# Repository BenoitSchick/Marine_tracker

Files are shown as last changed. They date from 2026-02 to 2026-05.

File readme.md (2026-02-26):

# 🌊 PI MONIT – Group 4  
## Marine Animal Tracking System  

**Schick Benoit · Warpelin Daryl · Jeyapalan Jeyapiragash · Zweifel Robin**

---

## 📌 Project Overview

This project focuses on the design of an embedded tracking module intended to be attached to marine animals.

The primary objective is to monitor animal movements in order to:

- Better understand behavioural patterns  
- Analyse migratory routes  
- Identify critical marine areas requiring protection  

Beyond behavioural research, marine animals provide a unique and valuable platform for carrying environmental sensors. Their ability to travel long distances and dive to great depths enables data collection in regions that are difficult — or impossible — for humans to access.

Our system is designed to measure **ocean temperature as a function of depth**, contributing to climate research. Ocean temperature plays a crucial role in regulating ocean currents, which in turn significantly influence the planet’s global thermal balance.

The device must satisfy both **animal tracking** and **oceanographic measurement** requirements, while operating reliably under extreme marine conditions.

---

## 🌊 Mechanical & Environmental Constraints

The module must withstand harsh deep-sea conditions for extended periods.

### Pressure Resistance

- Fully waterproof housing  
- Designed to resist pressures equivalent to **1,000 m depth** (to be confirmed)  
- Some marine species dive beyond 1,000 m  

### Corrosion & Environmental Resistance

- Long-term exposure to seawater  
- Resistance to:
  - Salinity  
  - Thermal variations  
  - Biological fouling  

### Duration

- Minimum operational lifespan: **1 month**  
- Corresponds to a typical migration cycle  

### Structural Integrity

- Housing must maintain mechanical integrity despite:
  - High pressure  
  - Temperature changes  
  - Continuous environmental stress  

---

## ⚡ Electronic Constraints & Specifications

The embedded system must operate autonomously for at least **one month**.

### Power Optimization Strategy

- Optimised electronic architecture  
- Deep sleep operating modes  
- Careful selection of ultra-low-power components  

### Required Sensors

The module must integrate:

- 🌡️ **Temperature sensor**  
- 📏 **Pressure sensor** (for depth measurement and data validation)

These measurements form the foundation of the ocean monitoring component of the project.

---

## 📍 Localisation System

A GPS module must be integrated to:

- Track the animal’s position  
- Associate environmental measurements with precise geographic coordinates  

Position data is essential for accurate mapping and scientific analysis.

---

## 📡 Data Communication

When the animal surfaces, the module must transmit collected data.

Because the system operates in open ocean environments, communication must be achieved via:

- 🛰️ **Satellite link** (global coverage solution)

The transmitted data is then:

- Stored in a central database  
- Prepared for processing and analysis  

---

## 📊 Data Processing & Visualisation

Collected data will be:

1. Processed and validated  
2. Made accessible via a web platform  
3. Presented through interactive visualisations  

The platform must also:

- Provide access to raw scientific data  
- Enable collaboration within the research community  

The final repository could be based on the EMODnet portal  
(European Marine Observation and Data Network).

---

## 🎯 Project Goals Summary

- ✔ Long-term autonomous marine monitoring  
- ✔ Behavioural tracking of marine species  
- ✔ Ocean temperature profiling by depth  
- ✔ Satellite-based data transmission  
- ✔ Open scientific data access  
- ✔ Contribution to climate research  

---

> PI MONIT aims to combine embedded systems engineering, oceanography, and data science to support marine conservation and climate research.

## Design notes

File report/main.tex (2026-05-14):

\documentclass[12pt]{article}

% Language setting
% Replace `english' with e.g. `spanish' to change the document language
\usepackage[T1]{fontenc}
\usepackage[english]{babel}

% Set page size and margins
% Replace `letterpaper' with`a4paper' for UK/EU standard size
\usepackage[a4paper,top=2.5cm,bottom=2.5cm,left=2cm,right=2cm,marginparwidth=1.75cm]{geometry}

% include graphics i.e images
\usepackage{graphicx}
\usepackage{fancyhdr} % headers
\usepackage[utf8]{inputenc}
\usepackage{gensymb}
\usepackage{subcaption}
\usepackage{array}
\usepackage{tabularx}
\usepackage{csvsimple}
\usepackage{titlesec}
\usepackage{lastpage}
\usepackage{pdfpages}
\usepackage{comment}
\usepackage{xcolor}
\usepackage{multirow}
\usepackage{verbatim}
\usepackage{bm}
% \usepackage{gensymb}
\usepackage{url}
\usepackage{amsmath}

\usepackage{lipsum}  

\setcounter{tocdepth}{1} % Exclude subsubsections from the table of contents

% include hyperlinks in the doc
\usepackage{hyperref}
%setup hyperref

\pagestyle{fancy}
\fancyhf{}
\rhead{\today}
\lhead{Marine Animal Tracking System}
\lfoot{PI - Wearable Sensing Device}
\rfoot{Page \thepage}
\renewcommand{\headrulewidth}{1pt}
\renewcommand{\footrulewidth}{1pt}

%------------------------------------------------------------------------------------------------
\title{PI}
\author{Benoit Schick}

\begin{document}

\begin{titlepage}
   \begin{center}
        \Huge
        Marine Animal Tracking System\\
        \Large 
        PI - Wearable Sensing Device 
            
        \vspace{1.5cm}
        \Large    
        Benoit Schick\\
        Warpelin Daryl\\
       	Jeyapalan Jeyapiragash\\
	Zweifel Robin
        
        \vspace{0.5cm}
        
        Supervisor:\\
        \vspace{0.1cm}
        Marco Mazza\\

        \vfill

        2024–2025 Academic Year, Spring Semester \\
        \vspace{1cm}
            
        \normalsize
        Multidisciplinary project\\
        \vspace{0.25cm}
        
	Master of science in Engineering 
        \vspace{0.25cm}
        
        \vspace{0.8cm}
            
        
        \vspace{1cm} 
        
   \end{center}
\end{titlepage}

\pagestyle{fancy}

\section{Hardware (Benoit Schick)}
\subsection{Défis et contraintes du système embarqué}

Le système développé dans ce projet doit fonctionner dans un environnement particulièrement contraignant, ce qui impose certains choix au niveau de l'architecture. 
\subsubsection{Isolement géographique}
L’une des contraintes fondamentales est la localisation des animaux suivis. Les espèces ciblées évoluent en haute mer, à des centaines voire des milliers de kilomètres de toute infrastructure terrestre. Dans ces zones, aucune technologie de communication classique n’est disponible : les réseaux cellulaires tels que le GSM, la 4G ou la 5G ne sont exploitables qu’à proximité des côtes, et les réseaux IoT longue portée comme LoRaWAN sont insuffisants pour cette application. \\
Dans ce contexte, la seule solution viable pour assurer une communication globale est la transmission par satellite. Deux technologies principales sont généralement utilisées dans ce type d’application :
\begin{itemize}
	\item \textbf{Le réseau Iridium} : Système qui repose sur une constellation de 66 satellites en orbite basse (LEO, ~780 km), offre une latence faible et une couverture totale.
	\item \textbf{Le réseau Argos} : Système satellite pour la localisation et la collecte de données désigné spécifiquement pour l'étude et la protection de l'environnement. Il est par exemple utilisé pour le suivi d'animaux marins et est largement adopté dans la communauté scientifique pour ce type d'application.  
\end{itemize}
Ces solutions permettent une communication globale mais introduisent des contraintes importantes en termes d’énergie et de disponibilité du signal.

\subsubsection{Contraintes du milieu marin}
Le milieu marin impose une contrainte majeure : l'eau de mer est un milieu extrêmement atténuant pour les ondes électromagnétiques utilisées pour la communication satellite. A quelques centimètres de profondeur seulement, tout signal est totalement absorbé et il est donc impossible de transmettre ou de recevoir quoi que ce soit lorsque l'animal est immergé, quelle que soit la puissance d'émission utillisée.\\
Cette contrainte impose un fonctionnement discontinu du système, alternant entre des phases d’immersion, où seules les mesures sont réalisées, et des phases de surface, où la communication est possible.

\subsubsection{Stockage temporaire}
L'impossibilité de transmission en continu des données exige d'intégrer une mémoire non volatile externe pour stocker temporairement l'ensemble des données acquises pendant les phases d'immersion (température, pression \footnote{Bien que fondamentale, la mesure de la pression a été abandonnée du à des contraintes budgétaires. Elle sera quand même évoquée dans ce rapport}, la position et horodatage des mesures). \\
Cette mémoire permet donc de gérer l’imprévisibilité des phases de surface, qui dépendent du comportement de l’animal et des conditions environnementales.

\subsubsection{Consommation}
Les conditions dans lequel le système va évoluer, introduit des contraintes importantes en termes de consommation énergétique. Les modules de communication, en particulier le GPS et le système satellite, figurent parmi les éléments les plus énergivores du système. \\
En effet, le module GPS nécessite une phase d’acquisition du signal satellite, qui peut devenir longue et coûteuse en énergie si les conditions de réception sont mauvaises ou si les fenêtres de surface sont très courtes. De même, le module de communication satellite présente des pics de consommation élevés lors de chaque tentative de transmission. \\
Ces contraintes sont aggravées par l’incertitude sur la durée et la fréquence des phases de surface, ce qui peut entraîner des activations répétées des modules de localisation et de communication, augmentant encore la consommation globale du système. \\

Or l’autonomie du système constitue un paramètre critique, car elle détermine la durée d’exploitation du dispositif ainsi que la capacité à le récupérer grâce au module GPS, chargé de transmettre la position du boîtier. Une stratégie de gestion énergétique est donc nécessaire afin de limiter le temps d'activation des modules GPS+satellite et maximiser le temps passé en mode low-power. Le système devra donc reposer sur une logique événementielle, dans laquelle les modules GPS et satellite ne sont activés que lorsque les conditions sont favorables, c’est-à-dire lors des phases de surface.

\subsection{Spécifications}

Le comportement de l’animal joue un rôle déterminant dans le dimensionnement du système. En effet, lorsqu’il est immergé, toute communication satellite est impossible. Le dispositif doit donc exploiter les phases de surface, durant lesquelles l’animal doit rester suffisamment longtemps pour permettre l’acquisition d’une position GPS ainsi que la transmission des données via le module satellite. La profondeur de plongée constitue également un paramètre critique, car elle impose des contraintes mécaniques importantes, notamment en raison de la pression exercée sur le boîtier. \\
Après comparaison avec d’autres espèces (cf. tableau), le choix s’est porté sur la tortue marine. Ce choix repose principalement sur ses phases de surface relativement régulières, qui facilitent l’établissement d’une connexion satellite fiable et limitent les activations inutiles des modules de communication et de localisation. Cela permet ainsi de réduire la consommation énergétique du système tout en simplifiant certaines contraintes mécaniques.\\

L’autonomie représente un autre enjeu majeur. Le système doit être capable de fonctionner sur une longue durée afin de collecter un volume de données suffisant, tout en permettant idéalement la récupération du dispositif en fin de mission afin de limiter son impact environnemental. Cela implique une gestion optimisée de l’énergie, notamment en réduisant l’utilisation des modules les plus énergivores.\\

% Enfin, l’environnement d’utilisation impose des contraintes fortes en termes de communication. En raison de l’éloignement des infrastructures terrestres, les solutions classiques (GSM, LoRa, etc.) ne sont pas exploitables. L’utilisation d’une liaison satellite est donc indispensable pour assurer la transmission des données sur de longues distances.

\noindent Voici un résumé des spécifications prises en compte pour la partie Hardware du projet :

\begin{itemize}
    \item \textbf{Communication} : Transmission des données via un réseau satellite.
    \item \textbf{Localisation} : Acquisition de la position GPS du dispositif afin de permettre sa localisation et sa récupération
    \item \textbf{Stockage} : Utilisation d'une mémoire non volatile permettant l’enregistrement des données durant les phases d’immersion.
    \item \textbf{Autonomie} : Fonctionnement sur batterie avec un objectif d’autonomie d’environ un mois, reposant sur une optimisation de la consommation (modes low power, activation événementielle des modules).
    \item \textbf{Capteurs} : Mesure de la température de l'eau et de la profondeur (via un capteur de pression) en fonction de la position, afin de constituer une base de données exploitable pour permettre de suivre l'évolution thermiques des océans dans le cadre du réchauffement climatique.  
\end{itemize}

\subsection{Architecture générale} 
La partie électronique doit assurer de manière autonome la localisation de l’animal, l’acquisition de données environnementales, le stockage temporaire des mesures ainsi que leur transmission vers une infrastructure terrestre via un lien satellite. L’ensemble de ces fonctions doit être garanti dans des conditions environnementales extrêmes (pression, salinité, immersion), tout en maintenant une autonomie énergétique suffisante.

\begin{figure}[h!]
	\centering
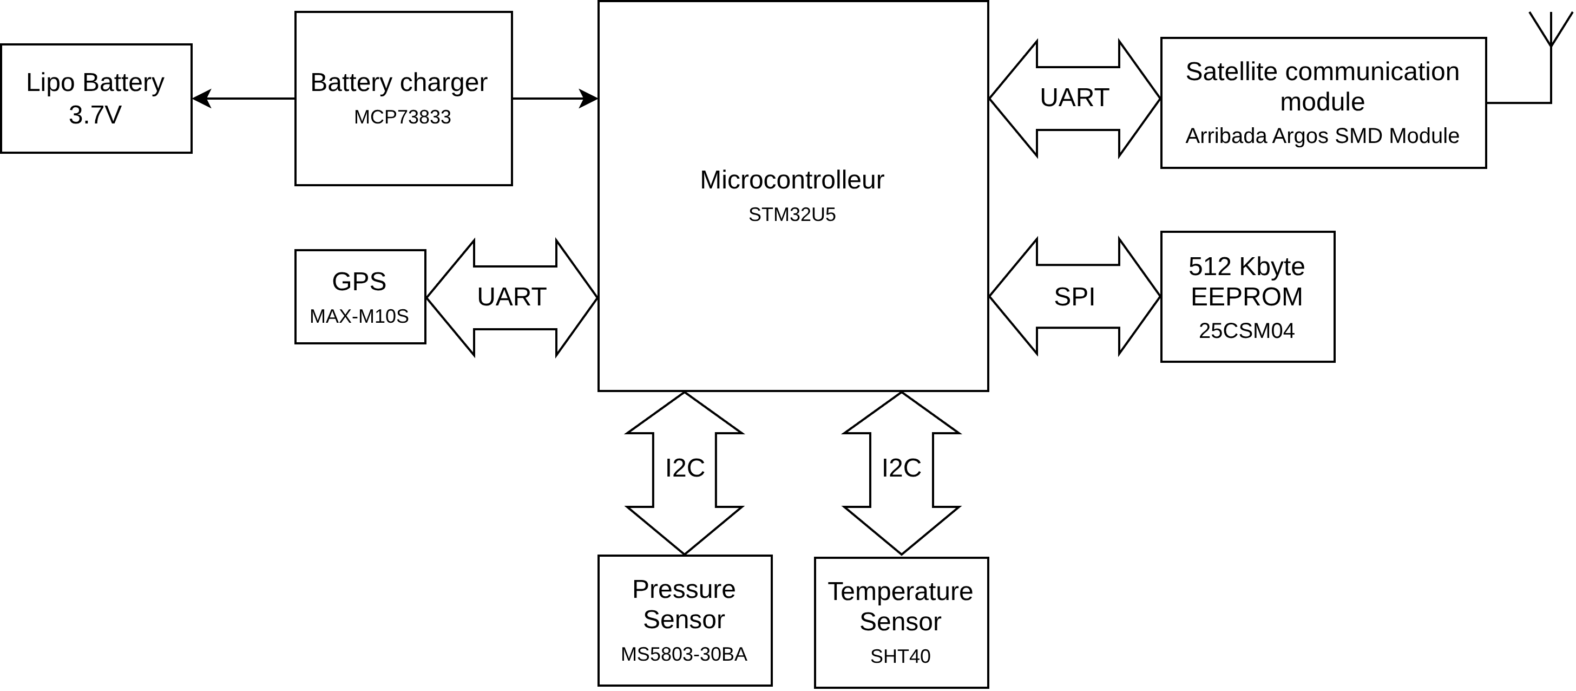
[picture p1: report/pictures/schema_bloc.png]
		
	\caption{Schéma bloc de la partie Hardware}
	\label{fig:schema_bloc}
\end{figure}

L’architecture du système s’articule autour d’un microcontrôleur STM32U5 basé sur un coeur ARM Cortex-M33. Ce composant a été retenu pour sa très faible consommation (jusqu’à 160 nA en mode low power), sa compatibilité avec Zephyr RTOS facilitant le développement logiciel, ainsi que la présence de multiples modes low-power (7 modes) permettant d’adapter le compromis entre consommation, disponibilité des périphériques et sources de wakeup. Il intègre également un large éventail d’interfaces de communication (I2C, SPI, UART, USB), assurant l’interconnexion avec les différents modules du système. \\

L’alimentation repose sur une batterie Lithium-Polymère (LiPo) 1S d’une capacité de 10 Ah. Ce choix s’explique par sa forte densité énergétique, permettant de optimiser l’énergie stockée tout en réduisant la masse et le volume (Fig. \ref{fig:densite_bat}), ce qui constitue un critère essentiel pour une application embarquée sur animal. Néanmoins, ce type de batterie impose des contraintes strictes en termes de sécurité et d'utilisation. \\
La gestion de la charge est assurée par le circuit MCP73833, qui intègre les protections nécessaires contre la surcharge et la décharge excessive. Dans cette phase de prototypage, la recharge s’effectue via une interface USB-C. À terme, une solution de récupération d’énergie est envisagée, basée sur un générateur entraîné par une hélice mise en rotation par les déplacements de l’animal.

\begin{figure}[h!]
	\centering
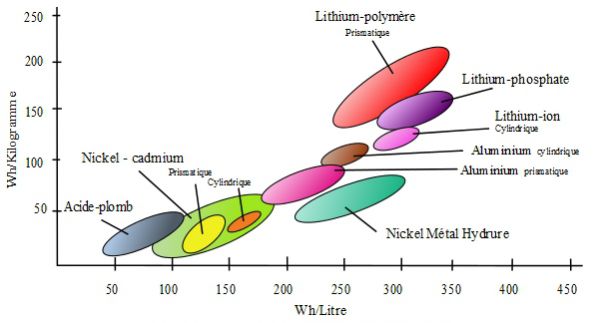
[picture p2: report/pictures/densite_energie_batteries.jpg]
		
	\caption{Densité d'énergie selon le type de batterie}
	\label{fig:densite_bat}
\end{figure}

La localisation est assurée par le module GPS MAX-M10S, sélectionné pour son faible niveau de consommation (environ 25mW en mode tracking continu), particulièrement adapté aux systèmes sur batterie. La communication avec le microcontrôleur s’effectue via une interface UART.\\
L’acquisition des données environnementales repose sur deux capteurs connectés au microcontrôleur via le bus I2C :
\begin{itemize}
	\item Capteur de pression MS5803-30BA : permet d’estimer la profondeur à partir de la pression mesurée. Sa capacité à supporter jusqu’à 30bar (environ 300m de profondeur) le rend adapté au suivi de tortues marines.
	\item Capteur de température et humidité SHT40 : mesure la température interne du boîtier ainsi que l’humidité, paramètre critique pour détecter toute infiltration. Ce capteur présente également une très faible consommation ($0.4\mu W$), compatible avec les contraintes énergétiques du système.
\end{itemize}

La transmission des données est assurée par un module de communication satellite Arribada Argos SMD, interfacé en UART avec le microcontrôleur. Ce module a été retenu pour son caractère open-source, facilitant l’intégration logicielle, ainsi que pour son coût plus accessible que les solutions Iridium. Il permet d’exploiter le réseau Argos, composé d’une constellation de satellites offrant une couverture mondiale adaptée à cette application. \\

Enfin, une mémoire non volatile EEPROM de 512kB assure le stockage tampon des données entre deux phases de transmission, garantissant la conservation des mesures en cas d’indisponibilité temporaire du lien satellite.

\subsection{Liste du matériel}

La Table \ref{tab:bom} présente la liste complète des composants intégrés sur le PCB. Le choix de ces derniers a été principalement guidé par des critères de faible consommation, de compacité et de disponibilité via le distributeur Digikey. \\
Pour des raisons de gains de temps, la fabrication ainsi que l’assemblage du PCB ont été confiés à PCBWay.

\begin{table}[h!]
\centering
\scriptsize
\setlength{\tabcolsep}{2.5pt}
\renewcommand{\arraystretch}{1.05}

\begin{tabularx}{\textwidth}{|c|c|c|c|c|X|}
\hline

\textbf{\rule{0pt}{3.2ex}\#} & 
\textbf{Reference} & 
\textbf{Qty} & 
\textbf{Mfr} & 
\textbf{Digikey Part Number} & 
\textbf{Description/Value} \\
\hline \hline

1 & Y3 & 1 & Epson & SER4396TR-ND & 16 MHz crystal \\ \hline
2 & Y1 & 1 & Epson & SER4071TR-ND & 32.768 kHz crystal (RTC) \\ \hline

3 & U7 & 1 & u-blox & 672-MAX-M10S-00BTR-ND & GNSS module \\ \hline
4 & U6 & 1 & Microchip & 150-25CSM04T-I/SNTR-ND & 4 Mbit SPI EEPROM \\ \hline
5 & U5 & 1 & Microchip & MCP1726-3302E/MF-ND & 3.3V LDO regulator \\ \hline
6 & U3 & 1 & Microchip & MCP73833T-FCI/MFTR-ND & LiPo charger \\ \hline
7 & U2 & 1 & Sensirion & 1649-SHT40-AD1B-R3TR-ND & Temp \& humidity sensor \\ \hline
8 & U1 & 1 & ST & 497-STM32U575RGT6-ND & Cortex-M33 MCU \\ \hline

9 & SW2 & 1 & C\&K & CKN12215-2-ND & Push button \\ \hline

10 & R12 & 1 & YAGEO & 311-2KLRTR-ND & 2k$\Omega$ \\ \hline
11 & R8--R10 & 3 & YAGEO & 311-470LRTR-ND & 470$\Omega$ \\ \hline
12 & R4,R7 & 2 & YAGEO & 311-5.10KLRTR-ND & 5.1k$\Omega$ \\ \hline
13 & R1--R6,R11 & 6 & YAGEO & 311-10.0KLRTR-ND & 10k$\Omega$ \\ \hline

14 & J6 & 1 & Samtec & 612-RSP-122811-01TR-ND & U.FL RF connector \\ \hline
15 & J5 & 1 & Würth & 732-5321-ND & 8-pin header \\ \hline
16 & J4 & 1 & JST & 455-BM04B-GHS-TBTTR-ND & 4-pin connector \\ \hline
17 & J3 & 1 & GCT & 2073-USB4215-03-ATR-ND & USB-C \\ \hline
18 & J2 & 1 & Amphenol & 609-3712-ND & SWD/JTAG \\ \hline
19 & J1 & 1 & Würth & 732-10955-ND & Terminal block \\ \hline

20 & D1--D3 & 3 & Rohm & SML-D12U1WT86TR-ND & Red LEDs \\ \hline

21 & C26 & 1 & YAGEO & 311-1785-2-ND & 4.7$\mu$F \\ \hline
22 & C22,C23 & 2 & YAGEO & 13-CC0603JPNPO9BN102TR-ND & 1nF \\ \hline
23 & C13,C14 & 2 & YAGEO & 311-1754-2-ND & 20pF \\ \hline
24 & C11,C12 & 2 & YAGEO & 311-1058-2-ND & 10pF \\ \hline
25 & C6,C7,C19,C28 & 4 & YAGEO & 311-1446-2-ND & 1$\mu$F \\ \hline
26 & C3--C10,C15--C17,C20,C21,C25 & 12 & YAGEO & 311-1088-2-ND & 100nF \\ \hline
27 & C2,C18,C24,C27,C29,C30 & 6 & YAGEO & 311-3502-2-ND & 10$\mu$F \\ \hline
28 & C1 & 1 & YAGEO & 311-1907-2-ND & 4.7$\mu$F \\ \hline

\end{tabularx}

\caption{Bill of Materials (BOM) – PCB}
\label{tab:bom}
\end{table}

Le tableau \ref{tab:component_suppl} regroupe les composants externes au PCB : les antennes, la batterie LiPo, le module satellite Arribada et le capteur de pression BlueRobotics. \\
Le module satellite a été externalisé pour des raisons d'encombrement car son intégration directe sur le PCB aurait conduit à des dimensions incompatibles avec les contraintes mécaniques du boîtier. Le capteur de pression, quant à lui, nécessite d'être monté sur la paroi du boîtier afin d'exposer sa membrane au milieu extérieur.

\begin{table}[h!]
\centering
\scriptsize
\setlength{\tabcolsep}{2.5pt}
\renewcommand{\arraystretch}{1.05}

\begin{tabularx}{\textwidth}{|c|c|c|c|X|}
\hline

\textbf{\rule{0pt}{3.2ex}\#} & 
\textbf{Name} & 
\textbf{Qty} & 
\textbf{Mfr} & 
\textbf{URL} \\ 
\hline \hline

29 & 30bars Pressure sensors & 1 & BlueRobotics & \url{https://bluerobotics.com/store/sensors-cameras/sensors/bar-depth-pressure-sensor}\\ \hline
30 & Lipo Battery 1S 10Ah & 1 & Uxney & \url{https://www.amazon.fr/dp/B0CSS4FFHC?th=1}\\ \hline
31 & Argos Omnidirectional Antenna (401Mhz) & 1 & Sparkfun & \url{https://www.sparkfun.com/argos-omnidirectional-antenna-401mhz.html}\\ \hline
32 & GNSS patch Antenna 1.6GHz & 1 & Quectel & \url{https://www.digikey.ch/en/products/detail/quectel/YFGA225E3BM/26239589}\\ \hline
33 & Arribada SMD Wing & 1 & Arribada & \url{https://arribada.org/product/arribada-smd-wing/}\\ \hline
\end{tabularx}

\caption{Listes des composants externes au PCB}
\label{tab:component_suppl}
\end{table}

\subsection{Estimation de l'autonomie du système}

Le mode de fonctionnement des différents modules dépend fortement du comportement de l’animal, notamment s’il alterne entre des phases d’immersion et des phases en surface. Ces deux états doivent être détectés par le système afin d’activer, par exemple, le GPS et le module satellite lorsque l’animal remonte à la surface. Pour cette raison, le fonctionnement global repose principalement sur un capteur de pression, capable de distinguer ces deux phases en mesurant la profondeur. \\

\noindent Le système alterne donc entre deux états principaux :

\begin{itemize}
    \item \textbf{Phase d’immersion} : les capteurs de température et de pression sont activés périodiquement afin d’effectuer les mesures. Les modules GPS et satellite restent en mode basse consommation.
    \item \textbf{Phase de surface} : activation du module GPS pour l’acquisition de la position, suivie de l’activation du module satellite pour la transmission des données. Seul le capteur de pression continue d’effectuer des mesures afin de détecter le moment où l’animal replonge, et ainsi éviter de maintenir inutilement le GPS et le module de communication actifs.

\end{itemize}

\subsubsection{Calcul de consommation}

Notre système est dimensionné pour une tortue marine. Si l’on choisit de réaliser \textbf{une mesure toutes les 5 minutes durant les phases d’immersion}, cela correspond à une mesure tous les 500 mètres, en supposant que l’animal se déplace à une vitesse moyenne de 5 km/h. \\
On suppose également que la tortue \textbf{remonte à la surface toutes les heures en moyenne} et y reste pendant 1 minute. Durant cette minute, le module satellite est activé afin de laisser suffisamment de temps au passage d’un satellite pour transmettre les données enregistrées. Le module GPS, quant à lui, n’est activé que pendant 5 secondes en mode warm start (cf. section \ref{sect:moduleGNSS} - Module GNSS). \\

\noindent À partir des consommations des différents modules (cf. Table \ref{tab:conso_phases}) et des hypothèses temporelles précédentes, il est possible d’estimer l’autonomie du système, alimenté par une batterie LiPo 1S de capacité 10 Ah.
\begin{table}[h]
\centering
\caption{Consommations des différents modules selon les phases de fonctionnement du système}
\begin{tabular}{|c|l|l|c|}
\hline
\textbf{Phase} & \textbf{Module} & \textbf{Mode} & \textbf{Courant} \\
\hline\hline

\multirow{3}{*}{Immersion}
& STM32U5 & Run Mode / Low Power & 2$mA$ / 50$\mu A$ \\
& SHT40 & Measurement / Low Power & 2.2$\mu A$ / 80 $nA$ \\
& MS5837-30BA & Measurement / Low Power & 5$\mu A$ / 10 $nA$ \\
& GPS MAX-M10S & Standby & 45$\mu A$ \\
& Module Argos & Low Power & 2$\mu A$ \\
\hline

\multirow{3}{*}{Surface}
& STM32U5 & Run Mode & $2mA$ \\
& SHT40 & Low Power & 80 $nA$ \\
& MS5837-30BA & Measurement / Low Power & 5$\mu A$ / 10 $nA$ \\
& GPS MAX-M10S & Tracking/Acquisition & $10mA$\footnote{il s'agit du courant moyen} \\
& Module Argos & Transmission & $250mA$ \\
\hline

\end{tabular}
\label{tab:conso_phases}
\end{table}

$\triangleright$ \textbf{Consommation en phase d’immersion} \\

\noindent Lors des phases d’immersion, le microcontrôleur STM32 ainsi que les deux capteurs fonctionnent sur des cycles de 5 minutes, comprenant 2 secondes de mesure puis le reste du temps en mode basse consommation. \\
Le courant moyen durant cette phase est estimé à :
\begin{align*}
I_{avgImm}
    &= I_{avgStm} + I_{avgSHT40} + I_{avgMS58} + I_{avgGPS} + I_{avgArgos} \\
    &= \left(\frac{2\,\mathrm{s}}{300\,\mathrm{s}} \cdot 2\,\mathrm{mA}
       + \frac{298\,\mathrm{s}}{300\,\mathrm{s}} \cdot 50\,\mu\mathrm{A}\right) \nonumber\\
    &\quad + \left(\frac{2\,\mathrm{s}}{300\,\mathrm{s}} \cdot 2.2\,\mu\mathrm{A}
       + \frac{298\,\mathrm{s}}{300\,\mathrm{s}} \cdot 80\,\mathrm{nA}\right) \nonumber\\
    &\quad + \left(\frac{2\,\mathrm{s}}{300\,\mathrm{s}} \cdot 5\,\mu\mathrm{A}
       + \frac{298\,\mathrm{s}}{300\,\mathrm{s}} \cdot 10\,\mathrm{nA}\right) \nonumber\\
    &\quad + 45\,\mu\mathrm{A} + 2\,\mu\mathrm{A} \\
    &= \mathbf{0.110\ \mathrm{mA}}
\end{align*}

$\triangleright$ \textbf{Consommation en phase de surface} \\

\noindent Lorsque l’animal remonte en surface, il y reste environ 1 minute par heure. Durant cette minute, et en négligeant la consommation des capteurs de pression/température, le courant moyen est donné par la somme des contributions du STM32, du GNSS et du module satellite, soit :
\begin{align*}
I_{avgSur} &= I_{avgStm} + I_{avgGPS} + I_{avgArgos} \\
	   &= 2mA + \frac{5s}{60s} \cdot 10mA + 250mA \\ 
	   &= \bm{252.8 mA}
\end{align*}

$\triangleright$ \textbf{Autonomie estimée} \\

\noindent Sur un cycle complet de 60 minutes, composé de 59 minutes d’immersion et d’1 minute en surface, le courant moyen total du système est :

\begin{equation}
	I_{moy} = \frac{59}{60} \cdot I_{avgImm} + \frac{1}{60} \cdot I_{avgSur} = \bm{4.3mA}
\end{equation}

\noindent En considérant une batterie de capacité 10 Ah, l’autonomie théorique du système est donnée par :

\begin{equation}
	Autonomie = \frac{10A}{I_{moy}} = \frac{10A}{4.3mA} \approx 2326h \approx 97j \approx \bm{3mois}   
\end{equation}

\subsection{Module GNSS}\label{sect:moduleGNSS}

% Cette section a pour objectif d'expliquer les différents modes de fonctionnement du module GNSS dans l'objectif d'optimiser sa consommation. En effet, il s'agit d'un des modules le plus énergivores et mérite donc un intérêt particulier à optimiser sa consommation. \\
% Le choix d'antenne est également critique car le signal GPS est extrêmement faible et son signal est très sensible. 
Cette section présente les différents modes de fonctionnement du module GNSS ainsi que la stratégie retenue pour en réduire la consommation énergétique. En effet, ce sous-système figure parmi les plus énergivores de l'architecture et nécessite donc une attention particulière. Le choix de l'antenne est également déterminant, les signaux GNSS reçus étant de très faible puissance et particulièrement sensibles aux perturbations.

\subsubsection{Types de démarrage}

Les récepteurs GNSS distinguent trois modes de démarrage selon les informations
disponibles à la mise sous tension :

\begin{itemize}
    \item \textbf{Cold start} : le récepteur ne dispose d'aucune information préalable (heure, dernière position, et  éphémérides\footnote{Données orbitales précises transmises par les satellites et décrivant leur trajectoire instantanée.}). Il doit alors rechercher les satellites visibles, synchroniser leurs signaux et télécharger les données nécessaires au calcul de position. Cette procédure conduit à un \textit{TTFF}\footnote{\textit{Time To First Fix}, temps nécessaire après la mise sous tension pour obtenir une position et une heure valides à partir d'au moins quatre satellites.} typiquement de l'ordre de 30 secondes et à une sensibilité réduite du récepteur (-148dBm).

    \item \textbf{Warm start} : le récepteur conserve une estimation de l'heure, de la dernière position connue ainsi que des informations globales sur la constellation. Les éphémérides précédemment mémorisées étant généralement plus valides après quelques heures, elles doivent être téléchargées à nouveau. Le \textit{TTFF} est alors réduit à quelques secondes et le récepteur dispose d'une bien meilleure sensibilité (-165dBm).

    \item \textbf{Hot start} : le récepteur dispose encore de données de navigation récentes et valides, notamment des éphémérides. Le redémarrage est quasi immédiat et ne nécessite pas de téléchargement complémentaire. Pour le module MAX-M10M, le \textit{TTFF} typique est de l'ordre de 1 seconde avec une sensibilité de -165dBm.
\end{itemize}

Les informations utilisées pour accélérer le redémarrage sont conservées dans la \textbf{Battery-Backed RAM (BBR)} du module. En cas de perte d'alimentation de cette mémoire, ces données sont effacées et le module redémarre en \textit{cold start}.

\subsubsection{Gestion de l'alimentation du module GNSS}

Les signaux GNSS étant fortement atténués par l'eau de mer dès quelques centimètres de profondeur, aucune réception exploitable n'est possible durant l'immersion. Afin de limiter la consommation pendant cette phase, le module est placé en mode deep sleep via le \textbf{Software Standby Mode}. Dans ce mode, l'alimentation interne est désactivée et le module suspend toute acquisition satellite. \\
Il est par contre impératif de maintenir l'alimentation du module GNSS (pin $V\_IO$) qui permet de conserver la mémoire BBR et l'horloge temp réel (RTC). Le GPS évitera ainsi un \textit{cold start} au redémarrage ce qui permet un \textit{TTFF} beaucoup plus rapide, un consommation réduite et également une sensibilité du récepteur bien meilleure (gain de 20dBm environ).\\

En pratique, le module reste en \textbf{Software Standby Mode} durant l'immersion avec $V\_IO$ maintenue en permanence ce qui représente une consommation d'environ $45\mu A$. Cette architecture permet un redémarrage en \textit{warm start} à chaque remontée en surface. 

\subsubsection{Antenne du GNSS}
L'antenne constitue un paramètre critique du récepteur GNSS : même le meilleur récepteur ne peut compenser les pertes engendrées par une antenne de mauvaise qualité ou une conception RF défaillante du PCB. Au-delà du choix et de la conception de l'antenne, son positionnement ainsi que l'environnement dans lequel elle opère peuvent impacter significativement ses performances. \\
Ainsi, pour garantir des performances optimales, le choix de l'antenne doit être guidé par les critères suivants :
\begin{enumerate}
\item \textbf{Faible directivité} : l’antenne doit présenter un diagramme de rayonnement suffisamment large afin de capter le plus grand nombre possible de satellites.
\item \textbf{Gain orienté vers le ciel :} Le gain de l'antenne doit être concentré vers la demi-sphère supérieure afin d'améliorer la sensibilité du récepteur. 
\item \textbf{Visibilité ciel dégagée :} L'antenne doit être positionnée de manière à disposer d'une vue dégagée vers le ciel, à l'écart de tout élément susceptible de perturber le champ électromagnétique, tel que des pièces métalliques ou des structures conductrices.
\item \textbf{Adaptation d’impédance} : l’impédance entre l’antenne, la ligne de transmission et l’entrée RF du récepteur GNSS doit être correctement adaptée (généralement à 50$\Omega$) afin de minimiser les réflexions et maximiser le transfert de puissance.
\end{enumerate}

Dans une optique de réduction de la consommation énergétique, le choix s’est porté sur une \textbf{antenne patch passive}. Ce choix se justifie principalement par l’absence de consommation propre à l’antenne, contrairement aux antennes actives qui intègrent un \textit{Low Noise Amplifier} (LNA), dont la consommation se situe typiquement entre 3 et 20mA.  Ce dernier permet néanmoins d'obtenir un gain plus élevé pour des dimensions plus compactes. \\
L’antenne patch passive, dépourvue d’amplification intégrée, impose en revanche une conception RF plus rigoureuse, notamment en raison d’une sensibilité accrue aux désadaptations d’impédance. Par ailleurs, ce type d’antenne nécessite un plan de masse de dimensions suffisantes afin d’assurer un gain satisfaisant ainsi qu’une directivité orientée vers le ciel. Plus ce plan de masse est réduit, plus les performances de l’antenne (gain, efficacité, rayonnement) se dégradent.

\begin{figure}[h]
	\centering	
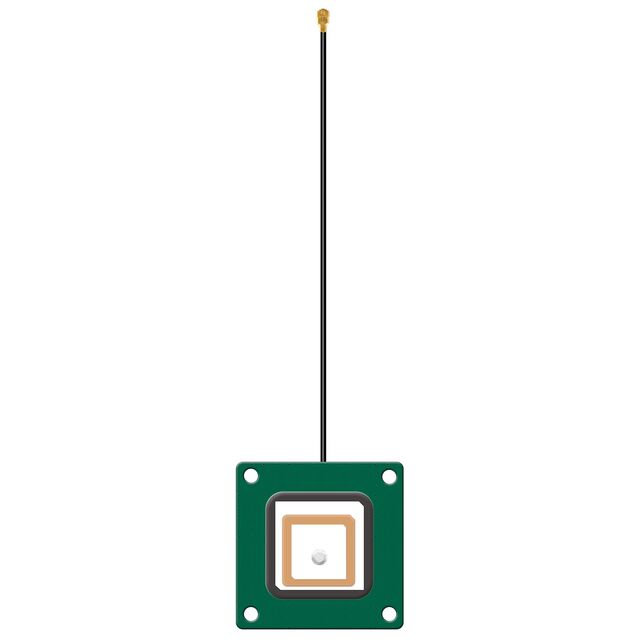
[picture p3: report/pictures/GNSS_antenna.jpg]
	
	\caption{Image de l'antenne patch chosie pour le récepteur GNSS}
	\label{fig:gnss_antenna}
\end{figure}

\subsubsection{Performances de l'antenne GNSS choisie}

Une antenne patch de chez Quectel a été retenue en raison de son large plan de masse (40 mm x 40 mm) (cf. fig. \ref{fig:gnss_antenna}). Celui-ci permet d’améliorer les performances de l’antenne patch en favorisant une directivité principalement orientée vers le ciel et en augmentant son gain (gain maximale de 0.58dBi), comme illustré aux figures \ref{fig:dia_ray} et \ref{fig:directivty}. \\
L’antenne patch étant destinée à être montée à plat, orientée vers le ciel, tout rayonnement non dirigé dans cette direction constitue une perte d’énergie. C’est précisément pour cette raison que cette antenne se révèle particulièrement adaptée à l’application visée. Elle satisfait aux exigences GNSS en offrant un bon compromis entre gain et couverture angulaire. \\
\begin{figure}[h]
    \centering
    \begin{minipage}[b]{0.45\textwidth}
        \centering
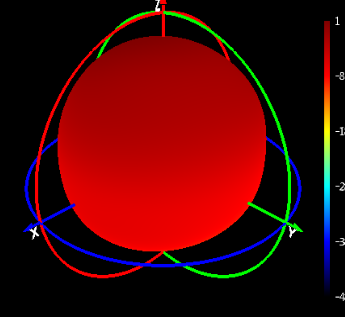
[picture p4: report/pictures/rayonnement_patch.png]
        
        \caption{Diagramme de rayonnement de l'antenne à la fréquence de 1575MHz (free space)}
	\label{fig:dia_ray}
    \end{minipage}
    \hfill
    \begin{minipage}[b]{0.45\textwidth}
        \centering
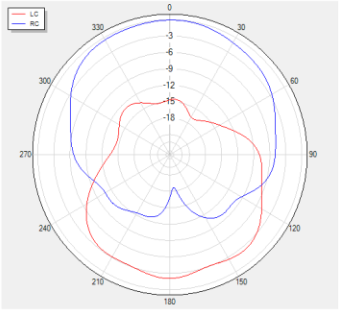
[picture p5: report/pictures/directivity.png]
        
        \caption{Directivité de l'antenne à Phi=0 degré et à une fréquence de 1575MHz (free space)}
	\label{fig:directivty}
    \end{minipage}
\end{figure}

La caractérisation complète d'une antenne ne saurait se limiter à l'analyse du diagramme de rayonnement et de la directivité ; l'adaptation d'impédance constitue également un paramètre fondamental. Ce dernier permet d'évaluer la proportion du signal réellement transmise au module GNSS. Il se mesure à l'aide d'un \textit{Vector Network Analyzer} (VNA).

\begin{figure}[h]
    \centering
    \begin{minipage}{0.45\textwidth}
        \centering
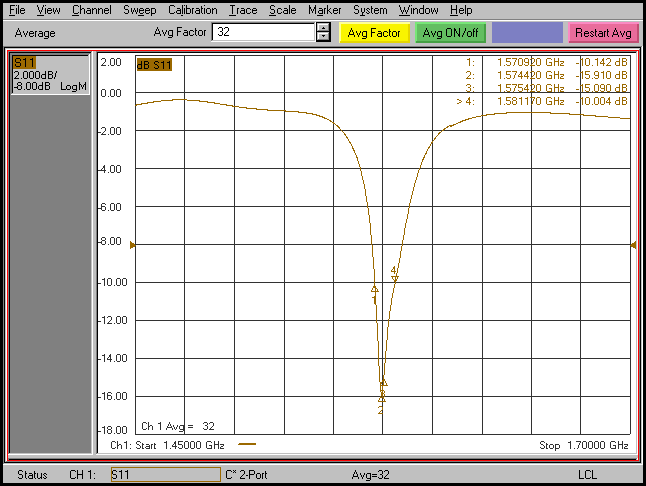
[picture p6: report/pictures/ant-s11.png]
        
        \caption{Paramètre S11 de l'antenne}
	\label{fig:s11}
    \end{minipage}
    \hfill
    \begin{minipage}{0.45\textwidth}
        \centering
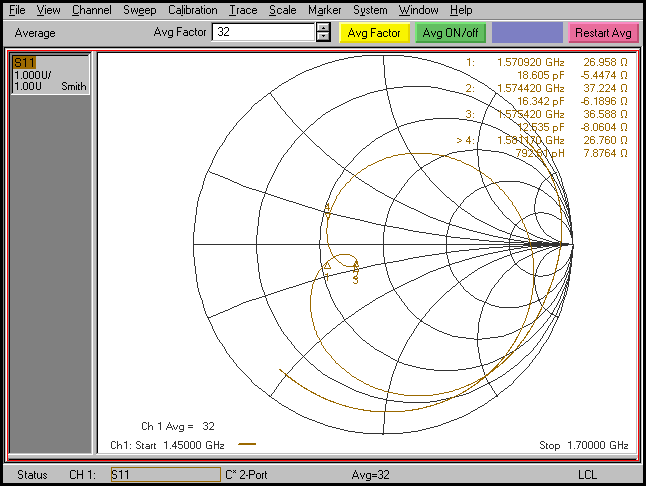
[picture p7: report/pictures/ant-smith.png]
        
        \caption{Smith Cart de l'antenne}
	\label{fig:smith_cart}
    \end{minipage}
\end{figure}

\noindent D'après la figure \ref{fig:s11}, le paramètre $S_{11}$ à 1.575GHz vaut -15.09dB, ce qui permet de déterminer le coefficient de réflexion $\Gamma$ :
\begin{equation}\label{eq:s11}
	S11 = 10 log(\Gamma) = -15.09dB \Leftrightarrow \Gamma = \frac{P_{reflechie}}{P_{transmise}} = 0.03  
\end{equation}

Ce résultat indique que \textbf{97\%} de la puissance incidente est transmise au récepteur GNSS, ce qui témoigne d'une excellente adaptation d'impédance. \\
L'impédance d'entrée de l'antenne peut alors être calculée à partir de $\Gamma$ (équation \ref{eq:s11}) :

\begin{equation}
	% Z = R + jX = 36.588 + \frac{1}{j\omega C} \Leftrightarrow \lvert Z \rvert = 	
	Z_{ant} = Z_0 \frac{1+\Gamma}{1-\Gamma} = \bm{53.09\Omega}
\end{equation}

Cette valeur est proche de l’objectif nominal de 50 $\Omega$. Ce résultat est également visible sur la carte de Smith : le marqueur 3, correspondant à la fréquence GNSS étudiée, est situé à proximité du centre de la carte, zone caractéristique d’une adaptation optimale (absence de réflexion).

Enfin, la figure \ref{fig:s11} permet également d’estimer la bande passante de l’antenne, définie conventionnellement par le critère $S_{11} < -10$ dB. À l’aide des marqueurs 1 et 4, la bande passante obtenue est d’environ \textbf{10.25 MHz}.

\subsection{Conception du PCB}
La conception du PCB a constitué une étape critique du projet. Une attention particulière a donc été portée au dimensionnement de l’alimentation, à la dissipation thermique et au routage de la piste RF du module GNSS.
\subsubsection{Dimensionnement de l'alimentation}
L'alimentation du PCB a été conçue pour supporter les pics de courants des modules de communication satellite et GNSS pouvant atteindre plusieurs centaines de milliampères sur de courtes durées. Si elle est mal dimensionné elle pourrait ne pas fournir ces appels de courants ou alors provoquer des chutes de tension susceptibles d'entrainer des dysfonctionnements. \\
Le choix des régulateurs, le routage des pistes d'alimentation ainsi que le découplage a été réalisé de manière à garantir une alimentation stable. \\

\begin{table}[h]
\centering
\caption{Pics de courants des modules satellite et GNSS}
\begin{tabular}{|c|l|}
\hline
\textbf{Module} & \textbf{Peak current} \\ 
\hline\hline
Satellite & 400mA \\
GNSS & 100mA \\
\hline
\end{tabular}
\label{tab:peak_current}
\end{table}

Le régulateur MCP1726 a ainsi été sélectionné pour sa capacité à fournir jusqu'à 1A, garantissant ainsi une marge suffisante face aux pics de courant estimés à 500mA. Il convient également de vérifier que le package retenu permet de dissiper correctement la chaleur générée, sans dépasser la température de jonction maximale admissible de 125°C (valeur tirée de la datasheet). \\ 

\noindent La puissance dissipée en interne par le LDO est donnée par :
\begin{equation}\label{eq:pLDO}
	P_{LDO} = (V_{IN(max)} - V_{OUT}) \times I_{OUT(max)} = (4.2V - 3.3V) \times 500mA = 0.45W	
\end{equation}
La température de jonction $T_J$ est calculée selon la formule issue de la datasheet :
\begin{equation}\label{eq:tj}
    T_J = T_A(\text{max}) + P_{LDO} \times R\theta_{JA}
\end{equation}
où $R\theta_{JA}$ est la résistance thermique junction-to-ambiant, exprimée en $^{\circ}C/W$, et $T_{A(max)}= 70^{\circ}C$, la température ambiante maximale supposée. \\

\noindent Deux packages sont disponibles pour le MCP1726 : le SOIC et le DFN. Seule ce dernier, qui dispose d'une résistance thermique bien inférieure (car il dispose d'un pad thermique) permet de respecter un température de jonction inférieur au 125$^{\circ}C$ spécifié. \\

\noindent Selon l'équation \ref{eq:tj}, la température de jonction atteint avec un boitier DFN de résistance thermique $R\theta_{JA} = 64^{\circ}C/W$ se calcul ainsi :
\begin{equation}
	T_J =	T_{JRISE} + T_A(max) = 0.45W \times 64^{\circ}C/W + 70^{\circ} C = 98.8^{\circ}C 
\end{equation}
Ainsi le package DFN est retenu, car il est le seul à garantir une température de jonction inférieure à 125$^{\circ}C$

\begin{figure}[h]
	\centering	
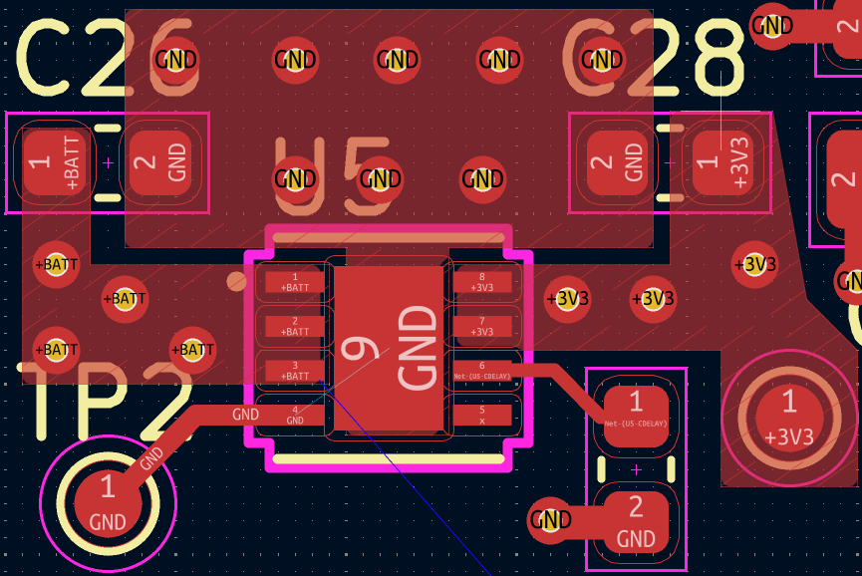
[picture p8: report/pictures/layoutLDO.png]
	
	\caption{Layout du régulateur LDO de sorte à assurer une bonne dissipation thermique}
	\label{fig:layoutLDO}
\end{figure}

\subsubsection{Layout du module GNSS}
Le signal reçu par le module GNSS est extrêmement faible, de l'ordre de −160dBm. La conception du layout RF constitue donc un point critique du PCB : toute perte ou perturbation sur la ligne RF peut dégrader significativement la sensibilité du récepteur et allonger le temps d'acquisition du signal. \\
Une attention particulière a été portée au routage de la liaison entre l'antenne et l'entrée RF du module. Cette ligne a été conçue comme une \textbf{ligne à impédance contrôlée de 50$\Omega$}  en utilisant une topologie \textit{Coplanar Waveguide with Ground} (CPWG), afin d'assurer un transfert de puissance optimal et de minimiser les réflexions. \\

\begin{figure}[h]
	\centering	
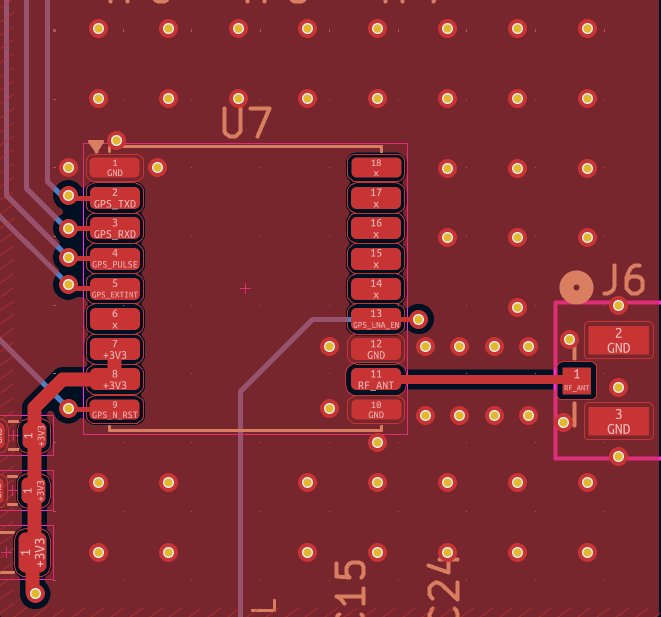
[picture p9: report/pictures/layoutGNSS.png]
	
	\caption{Layout du module GNSS}
	\label{fig:layoutGNSS}
\end{figure}

\subsubsection{Points de tests}
Enfin, plusieurs points de test ont été intégrés sur le PCB afin de faciliter l’accès aux principales alimentations, interfaces de communication et signaux critiques, simplifiant les mesures à l’oscilloscope ainsi que les phases de diagnostic.

\newpage
\section{Annexes}

% \subsection{Influence du plan de masse sur les performances d'une antenne patch (Benoit Schick)}
% Afin d’observer l’impact réel du plan de masse sur les performances de l’antenne, il est pertinent de comparer l’antenne patch passive retenue pour ce projet (Digikey part number: 2958-YFGA225E3BM-ND), dotée d’un large plan de masse, à une autre antenne patch passive (Digikey part number: 2958-YFGA012E3BM-ND) du même fabricant disposant d'un plan de masse plus réduit.

% \begin{figure}[h]
%     \centering
%     \begin{minipage}{0.45\textwidth}
%         \centering
%         \includegraphics[width=0.5\linewidth]{pictures/antenne_nul/ant_avecplan.png}
%         \subcaption{Antenne patch avec un plan de masse}
%     \end{minipage}
%     \hfill
%     \begin{minipage}{0.45\textwidth}
%         \centering
%         \includegraphics[width=0.5\linewidth]{pictures/antenne_nul/ant_sansplan.png}
%         \subcaption{Antenne patch sans plan de masse}
%     \end{minipage}
% \end{figure}

% \begin{figure}[h]
%     \centering
%     \begin{minipage}{0.45\textwidth}
%         \centering
%         \includegraphics[width=\linewidth]{pictures/antenne_nul/gain_avecplan.png}
%         \subcaption{Gain de l'antenne avec un plan de masse}
%     \end{minipage}
%     \hfill
%     \begin{minipage}{0.45\textwidth}
%         \centering
%         \includegraphics[width=\linewidth]{pictures/antenne_nul/gain_sansplan.png}
%         \subcaption{Gain de l'antenne sans plan de masse}
%     \end{minipage}
%     \caption{Influence du plan de masse sur le gain d'une antenne}
% \end{figure}

% \begin{figure}[h]
%     \centering
%     \begin{minipage}{0.45\textwidth}
%         \centering
%         \includegraphics[width=\linewidth]{pictures/antenne_nul/eff_avecplan.png}
%         \subcaption{Efficacité de l'antenne avec un plan de masse}
%     \end{minipage}
%     \hfill
%     \begin{minipage}{0.45\textwidth}
%         \centering
%         \includegraphics[width=\linewidth]{pictures/antenne_nul/eff_sansplan.png}
%         \subcaption{Efficacité de l'antenne sans plan de masse}
%     \end{minipage}
%     \caption{Influence du plan de masse sur l'efficacité d'une antenne}
% \end{figure}

% \begin{figure}[h]
%     \centering
%     \begin{minipage}{0.45\textwidth}
%         \centering
%         \includegraphics[width=\linewidth]{pictures/antenne_nul/dir_avecplan.png}
%         \subcaption{Directivité de l'antenne avec un plan de masse}
%     \end{minipage}
%     \hfill
%     \begin{minipage}{0.45\textwidth}
%         \centering
%         \includegraphics[width=\linewidth]{pictures/antenne_nul/dir_sansplan.png}
%         \subcaption{Directivité de l'antenne sans plan de masse}
%     \end{minipage}
%     \caption{Influence du plan de masse sur la directivité d'une antenne}
% \end{figure}

\subsection{Schematic}

\begin{figure}[h!]
	\centering	
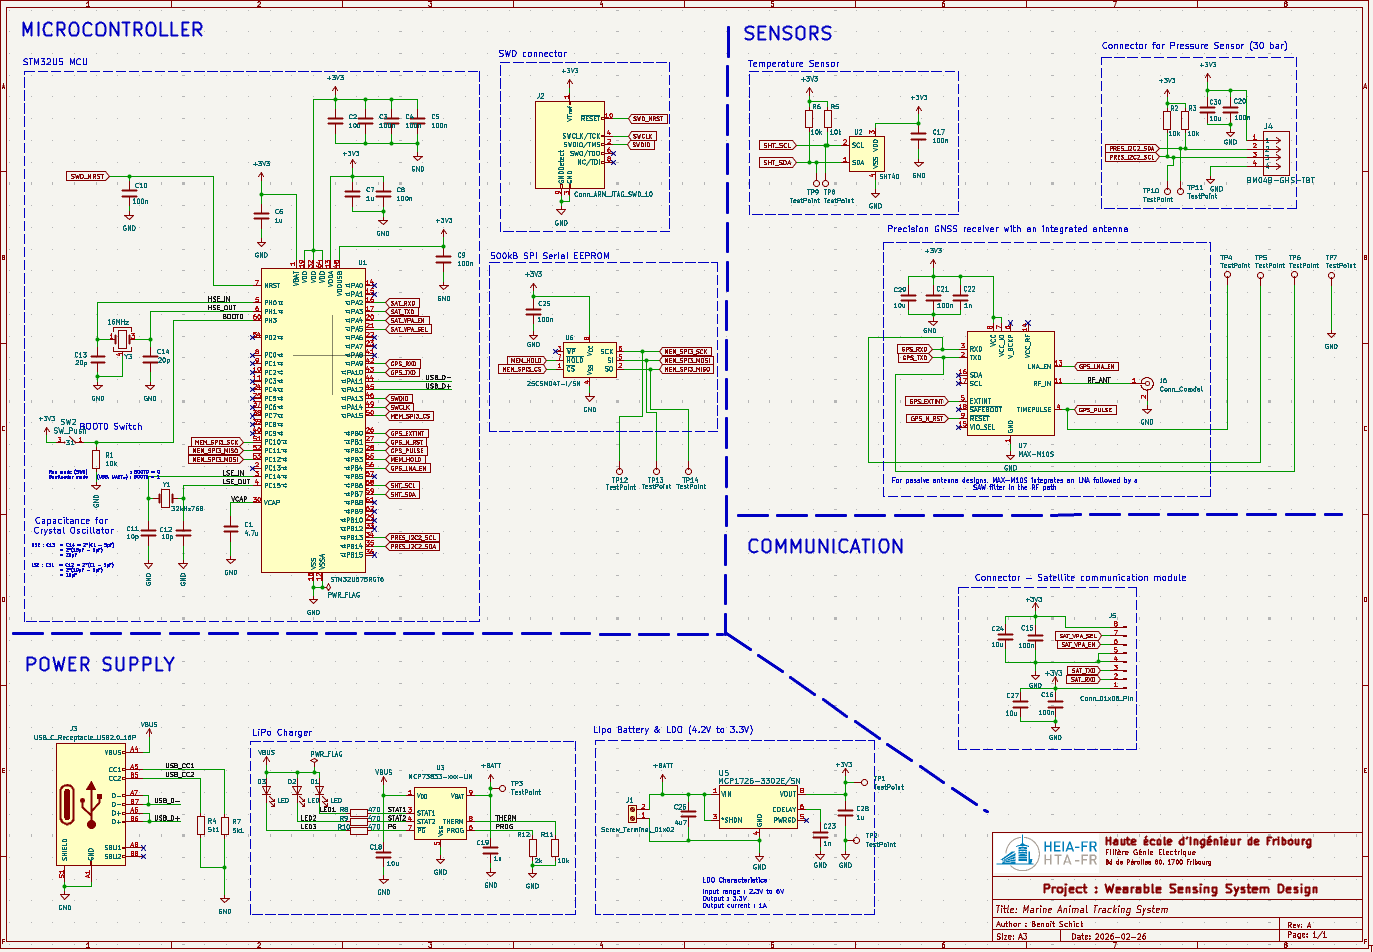
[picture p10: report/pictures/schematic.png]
	
	\caption{Schéma du circuit}
\end{figure}

\subsection{PCB}

\begin{figure}[h!]
	\centering	
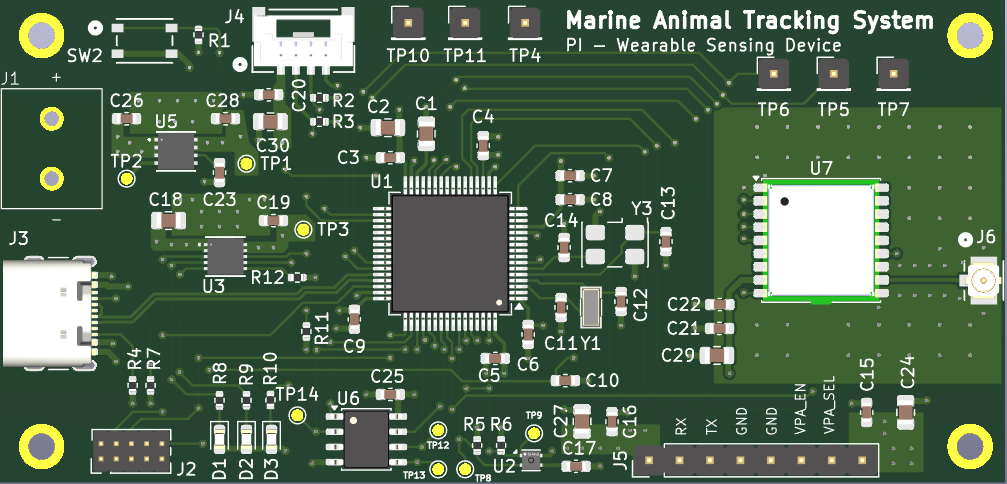
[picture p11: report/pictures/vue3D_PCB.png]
	
	\caption{Vue 3D du PCB}
\end{figure}

\end{document}

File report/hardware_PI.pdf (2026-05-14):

# Marine Animal Tracking System

## PI - Wearable Sensing Device

## Benoit Schick Warpelin Daryl Jeyapalan Jeyapiragash Zweifel Robin

## Supervisor:

## Marco Mazza

## 2024–2025 Academic Year, Spring Semester

Multidisciplinary project

Master of science in Engineering

Marine Animal Tracking System | May 14, 2026

## 1 Hardware (Benoit Schick)

### 1.1 Défis et contraintes du système embarqué

Le système développé dans ce projet doit fonctionner dans un environnement particulièrement contraignant, ce qui impose certains choix au niveau de l’architecture.

### 1.1.1 Isolement géographique

L’une des contraintes fondamentales est la localisation des animaux suivis. Les espèces ciblées évoluent en haute mer, à des centaines voire des milliers de kilomètres de toute infrastructure terrestre. Dans ces zones, aucune technologie de communication classique n’est disponible : les réseaux cellulaires tels que le GSM, la 4G ou la 5G ne sont exploitables qu’à proximité des côtes, et les réseaux IoT longue portée comme LoRaWAN sont insuffisants pour cette application. Dans ce contexte, la seule solution viable pour assurer une communication globale est la transmission par satellite. Deux technologies principales sont généralement utilisées dans ce type d’application :

- Le réseau Iridium : Système qui repose sur une constellation de 66 satellites en orbite basse (LEO, 780 km), offre une latence faible et une couverture totale.
- Le réseau Argos : Système satellite pour la localisation et la collecte de données désigné spécifiquement pour l’étude et la protection de l’environnement. Il est par exemple utilisé pour le suivi d’animaux marins et est largement adopté dans la communauté scientifique pour ce type d’application.

Ces solutions permettent une communication globale mais introduisent des contraintes importantes en termes d’énergie et de disponibilité du signal.

### 1.1.2 Contraintes du milieu marin

Le milieu marin impose une contrainte majeure : l’eau de mer est un milieu extrêmement atténuant pour les ondes électromagnétiques utilisées pour la communication satellite. A quelques centimètres de profondeur seulement, tout signal est totalement absorbé et il est donc impossible de transmettre ou de recevoir quoi que ce soit lorsque l’animal est immergé, quelle que soit la puissance d’émission utillisée.
Cette contrainte impose un fonctionnement discontinu du système, alternant entre des phases d’immersion, où seules les mesures sont réalisées, et des phases de surface, où la communication est possible.

### 1.1.3 Stockage temporaire

L’impossibilité de transmission en continu des données exige d’intégrer une mémoire non volatile externe pour stocker temporairement l’ensemble des données acquises pendant les phases d’immersion (température, pression 1
, la position et horodatage des mesures). Cette mémoire permet donc de gérer l’imprévisibilité des phases de surface, qui dépendent du comportement de l’animal et des conditions environnementales.

1Bien que fondamentale, la mesure de la pression a été abandonnée du à des contraintes budgétaires. Elle sera quand même évoquée dans ce rapport

PI - Wearable Sensing Device | Page 1

### 1.1.4 Consommation

Les conditions dans lequel le système va évoluer, introduit des contraintes importantes en termes de consommation énergétique. Les modules de communication, en particulier le GPS et le système satellite, figurent parmi les éléments les plus énergivores du système.
En effet, le module GPS nécessite une phase d’acquisition du signal satellite, qui peut devenir longue et coûteuse en énergie si les conditions de réception sont mauvaises ou si les fenêtres de surface sont très courtes. De même, le module de communication satellite présente des pics de consommation élevés lors de chaque tentative de transmission.
Ces contraintes sont aggravées par l’incertitude sur la durée et la fréquence des phases de surface, ce qui peut entraîner des activations répétées des modules de localisation et de communication, augmentant encore la consommation globale du système.

Or l’autonomie du système constitue un paramètre critique, car elle détermine la durée d’exploitation du dispositif ainsi que la capacité à le récupérer grâce au module GPS, chargé de transmettre la position du boîtier. Une stratégie de gestion énergétique est donc nécessaire afin de limiter le temps d’activation des modules GPS+satellite et maximiser le temps passé en mode low-power. Le système devra donc reposer sur une logique événementielle, dans laquelle les modules GPS et satellite ne sont activés que lorsque les conditions sont favorables, c’est-àdire lors des phases de surface.

### 1.2 Spécifications

Le comportement de l’animal joue un rôle déterminant dans le dimensionnement du système. En effet, lorsqu’il est immergé, toute communication satellite est impossible. Le dispositif doit donc exploiter les phases de surface, durant lesquelles l’animal doit rester suffisamment longtemps pour permettre l’acquisition d’une position GPS ainsi que la transmission des données via le module satellite. La profondeur de plongée constitue également un paramètre critique, car elle impose des contraintes mécaniques importantes, notamment en raison de la pression exercée sur le boîtier.
Après comparaison avec d’autres espèces (cf. tableau), le choix s’est porté sur la tortue marine. Ce choix repose principalement sur ses phases de surface relativement régulières, qui facilitent l’établissement d’une connexion satellite fiable et limitent les activations inutiles des modules de communication et de localisation. Cela permet ainsi de réduire la consommation énergétique du système tout en simplifiant certaines contraintes mécaniques.

L’autonomie représente un autre enjeu majeur. Le système doit être capable de fonctionner sur une longue durée afin de collecter un volume de données suffisant, tout en permettant idéalement la récupération du dispositif en fin de mission afin de limiter son impact environnemental. Cela implique une gestion optimisée de l’énergie, notamment en réduisant l’utilisation des modules les plus énergivores.

Voici un résumé des spécifications prises en compte pour la partie Hardware du projet :

- Communication : Transmission des données via un réseau satellite.
- Localisation : Acquisition de la position GPS du dispositif afin de permettre sa localisation et sa récupération

- Stockage : Utilisation d’une mémoire non volatile permettant l’enregistrement des données durant les phases d’immersion.
- Autonomie : Fonctionnement sur batterie avec un objectif d’autonomie d’environ un mois, reposant sur une optimisation de la consommation (modes low power, activation événementielle des modules).
- Capteurs : Mesure de la température de l’eau et de la profondeur (via un capteur de pression) en fonction de la position, afin de constituer une base de données exploitable pour permettre de suivre l’évolution thermiques des océans dans le cadre du réchauffement climatique.

### 1.3 Architecture générale

La partie électronique doit assurer de manière autonome la localisation de l’animal, l’acquisition de données environnementales, le stockage temporaire des mesures ainsi que leur transmission vers une infrastructure terrestre via un lien satellite. L’ensemble de ces fonctions doit être garanti dans des conditions environnementales extrêmes (pression, salinité, immersion), tout en maintenant une autonomie énergétique suffisante.


Figure 1: Schéma bloc de la partie Hardware

L’architecture du système s’articule autour d’un microcontrôleur STM32U5 basé sur un coeur ARM Cortex-M33. Ce composant a été retenu pour sa très faible consommation (jusqu’à 160 nA en mode low power), sa compatibilité avec Zephyr RTOS facilitant le développement logiciel, ainsi que la présence de multiples modes low-power (7 modes) permettant d’adapter le compromis entre consommation, disponibilité des périphériques et sources de wakeup. Il intègre également un large éventail d’interfaces de communication (I2C, SPI, UART, USB), assurant l’interconnexion avec les différents modules du système.

L’alimentation repose sur une batterie Lithium-Polymère (LiPo) 1S d’une capacité de 10 Ah. Ce choix s’explique par sa forte densité énergétique, permettant de optimiser l’énergie stockée tout en réduisant la masse et le volume (Fig. 2), ce qui constitue un critère essentiel pour une application embarquée sur animal. Néanmoins, ce type de batterie impose des contraintes strictes en termes de sécurité et d’utilisation.
La gestion de la charge est assurée par le circuit MCP73833, qui intègre les protections nécessaires contre la surcharge et la décharge excessive. Dans cette phase de prototypage, la recharge s’effectue via une interface USB-C. À terme, une solution de récupération d’énergie est envisagée, basée sur un générateur entraîné par une hélice mise en rotation par les déplacements de l’animal.


Figure 2: Densité d’énergie selon le type de batterie

La localisation est assurée par le module GPS MAX-M10S, sélectionné pour son faible niveau de consommation (environ 25mW en mode tracking continu), particulièrement adapté aux systèmes sur batterie. La communication avec le microcontrôleur s’effectue via une interface UART.
L’acquisition des données environnementales repose sur deux capteurs connectés au microcontrôleur via le bus I2C :
- Capteur de pression MS5803-30BA : permet d’estimer la profondeur à partir de la pression mesurée. Sa capacité à supporter jusqu’à 30bar (environ 300m de profondeur) le rend adapté au suivi de tortues marines.
- Capteur de température et humidité SHT40 : mesure la température interne du boîtier ainsi que l’humidité, paramètre critique pour détecter toute infiltration. Ce capteur présente également une très faible consommation (0.4µW), compatible avec les contraintes énergétiques du système.

La transmission des données est assurée par un module de communication satellite Arribada Argos SMD, interfacé en UART avec le microcontrôleur. Ce module a été retenu pour son caractère open-source, facilitant l’intégration logicielle, ainsi que pour son coût plus accessible que les solutions Iridium. Il permet d’exploiter le réseau Argos, composé d’une constellation de satellites offrant une couverture mondiale adaptée à cette application.

Enfin, une mémoire non volatile EEPROM de 512kB assure le stockage tampon des données entre deux phases de transmission, garantissant la conservation des mesures en cas d’indisponibilité temporaire du lien satellite.

### 1.4 Liste du matériel

La Table 1 présente la liste complète des composants intégrés sur le PCB. Le choix de ces derniers a été principalement guidé par des critères de faible consommation, de compacité et de disponibilité via le distributeur Digikey.
Pour des raisons de gains de temps, la fabrication ainsi que l’assemblage du PCB ont été confiés à PCBWay.
# | Reference | Qty | Mfr | Digikey Part Number | Description/Value

1 | Y3 | 1 | Epson | SER4396TR-ND | 16 MHz crystal
2 | Y1 | 1 | Epson | SER4071TR-ND | 32.768 kHz crystal (RTC)
3 | U7 | 1 | u-blox | 672-MAX-M10S-00BTR-ND | GNSS module
4 | U6 | 1 | Microchip | 150-25CSM04T-I/SNTR-ND | 4 Mbit SPI EEPROM
5 | U5 | 1 | Microchip | MCP1726-3302E/MF-ND | 3.3V LDO regulator
6 | U3 | 1 | Microchip | MCP73833T-FCI/MFTR-ND | LiPo charger
7 | U2 | 1 | Sensirion | 1649-SHT40-AD1B-R3TR-ND | Temp & humidity sensor
8 | U1 | 1 | ST | 497-STM32U575RGT6-ND | Cortex-M33 MCU
9 | SW2 | 1 | C&K | CKN12215-2-ND | Push button
10 | R12 | 1 | YAGEO | 311-2KLRTR-ND | 2kΩ
11 | R8–R10 | 3 | YAGEO | 311-470LRTR-ND | 470Ω
12 | R4,R7 | 2 | YAGEO | 311-5.10KLRTR-ND | 5.1kΩ
13 | R1–R6,R11 | 6 | YAGEO | 311-10.0KLRTR-ND | 10kΩ
14 | J6 | 1 | Samtec | 612-RSP-122811-01TR-ND | U.FL RF connector
15 | J5 | 1 | Würth | 732-5321-ND | 8-pin header
16 | J4 | 1 | JST | 455-BM04B-GHS-TBTTR-ND | 4-pin connector
17 | J3 | 1 | GCT | 2073-USB4215-03-ATR-ND | USB-C
18 | J2 | 1 | Amphenol | 609-3712-ND | SWD/JTAG
19 | J1 | 1 | Würth | 732-10955-ND | Terminal block
20 | D1–D3 | 3 | Rohm | SML-D12U1WT86TR-ND | Red LEDs
21 | C26 | 1 | YAGEO | 311-1785-2-ND | 4.7µF
22 | C22,C23 | 2 | YAGEO | 13-CC0603JPNPO9BN102TR-ND | 1nF
23 | C13,C14 | 2 | YAGEO | 311-1754-2-ND | 20pF
24 | C11,C12 | 2 | YAGEO | 311-1058-2-ND | 10pF
25 | C6,C7,C19,C28 | 4 | YAGEO | 311-1446-2-ND | 1µF
26 | C3–C10,C15–C17,C20,C21,C25 | 12 | YAGEO | 311-1088-2-ND | 100nF
27 | C2,C18,C24,C27,C29,C30 | 6 | YAGEO | 311-3502-2-ND | 10µF
28 | C1 | 1 | YAGEO | 311-1907-2-ND | 4.7µF

Table 1: Bill of Materials (BOM) – PCB

Le tableau 2 regroupe les composants externes au PCB : les antennes, la batterie LiPo, le module satellite Arribada et le capteur de pression BlueRobotics.
Le module satellite a été externalisé pour des raisons d’encombrement car son intégration directe sur le PCB aurait conduit à des dimensions incompatibles avec les contraintes mécaniques du boîtier. Le capteur de pression, quant à lui, nécessite d’être monté sur la paroi du boîtier afin d’exposer sa membrane au milieu extérieur.
# | Name | Qty | Mfr | URL

29 | 30bars Pressure sensors | 1 | BlueRobotics | https://bluerobotics.com/store/sensors-cameras/sensors/bar-depth-pressure-sensor (https://bluerobotics.com/store/sensors-cameras/sensors/bar-depth-pressure-sensor)
30 | Lipo Battery 1S 10Ah | 1 | Uxney | https://www.amazon.fr/dp/B0CSS4FFHC?th=1
| | | | html (https://www.sparkfun.com/argos-omnidirectional-antenna-401mhz.html)
32 | GNSS patch Antenna 1.6GHz | 1 | Quectel | https://www.digikey.ch/en/products/detail/quectel/YFGA225E3BM/26239589 (https://www.digikey.ch/en/products/detail/quectel/YFGA225E3BM/26239589)
33 | Arribada SMD Wing | 1 | Arribada | https://arribada.org/product/arribada-smd-wing/
31 | Argos Omnidirectional Antenna (401Mhz) | 1 | Sparkfun | https://www.sparkfun.com/argos-omnidirectional-antenna-401mhz.

Table 2: Listes des composants externes au PCB

### 1.5 Estimation de l’autonomie du système

Le mode de fonctionnement des différents modules dépend fortement du comportement de l’animal, notamment s’il alterne entre des phases d’immersion et des phases en surface. Ces deux états doivent être détectés par le système afin d’activer, par exemple, le GPS et le module satellite lorsque l’animal remonte à la surface. Pour cette raison, le fonctionnement global repose principalement sur un capteur de pression, capable de distinguer ces deux phases en mesurant la profondeur.

Le système alterne donc entre deux états principaux :

- Phase d’immersion : les capteurs de température et de pression sont activés périodiquement afin d’effectuer les mesures. Les modules GPS et satellite restent en mode basse consommation.
- Phase de surface : activation du module GPS pour l’acquisition de la position, suivie de l’activation du module satellite pour la transmission des données. Seul le capteur de pression continue d’effectuer des mesures afin de détecter le moment où l’animal replonge, et ainsi éviter de maintenir inutilement le GPS et le module de communication actifs.

### 1.5.1 Calcul de consommation

Notre système est dimensionné pour une tortue marine. Si l’on choisit de réaliser une mesure toutes les 5 minutes durant les phases d’immersion, cela correspond à une mesure tous les 500 mètres, en supposant que l’animal se déplace à une vitesse moyenne de 5 km/h.
On suppose également que la tortue remonte à la surface toutes les heures en moyenne et y reste pendant 1 minute. Durant cette minute, le module satellite est activé afin de laisser suffisamment de temps au passage d’un satellite pour transmettre les données enregistrées. Le module GPS, quant à lui, n’est activé que pendant 5 secondes en mode warm start (cf. section 1.6 - Module GNSS).

À partir des consommations des différents modules (cf. Table 3) et des hypothèses temporelles précédentes, il est possible d’estimer l’autonomie du système, alimenté par une batterie LiPo 1S de capacité 10 Ah.

Table 3: Consommations des différents modules selon les phases de fonctionnement du système

Phase | Module | Mode | Courant
Immersion | STM32U5 SHT40 MS5837-30BA GPS MAX-M10S Module Argos | Run Mode / Low Power Measurement / Low Power Measurement / Low Power Standby Low Power | 2mA / 50µA 2.2µA / 80 nA 5µA / 10 nA 45µA 2µA
Surface | STM32U5 SHT40 MS5837-30BA GPS MAX-M10S Module Argos | Run Mode Low Power Measurement / Low Power Tracking/Acquisition Transmission | 2mA 80 nA 5µA / 10 nA 10mA² 250mA

▷ Consommation en phase d’immersion

Lors des phases d’immersion, le microcontrôleur STM32 ainsi que les deux capteurs fonctionnent sur des cycles de 5 minutes, comprenant 2 secondes de mesure puis le reste du temps en mode

basse consommation.
Le courant moyen durant cette phase est estimé à :

IavgImm = IavgStm + IavgSHT40 + IavgMS58 + IavgGP S + IavgArgos

=

2 s
300 s
- 2 mA + 298 s
300 s
- 50 µA

+

2 s
300 s
- 2.2 µA + 298 s
300 s
- 80 nA

+

2 s
300 s
- 5 µA + 298 s
300 s
- 10 nA

+ 45 µA + 2 µA
= 0.110 mA

▷ Consommation en phase de surface

Lorsque l’animal remonte en surface, il y reste environ 1 minute par heure. Durant cette minute, et en négligeant la consommation des capteurs de pression/température, le courant moyen est donné par la somme des contributions du STM32, du GNSS et du module satellite, soit :

IavgSur = IavgStm + IavgGP S + IavgArgos

= 2mA +

5s
60s
- 10mA + 250mA

= 252.8mA

▷ Autonomie estimée

Sur un cycle complet de 60 minutes, composé de 59 minutes d’immersion et d’1 minute en surface, le courant moyen total du système est :

Imoy =

59
60
- IavgImm +

1
60
- IavgSur = 4.3mA | (1)

En considérant une batterie de capacité 10 Ah, l’autonomie théorique du système est donnée par :

Autonomie =

10A

Imoy

=

10A
4.3mA
≈ 2326h ≈ 97j ≈ 3mois | (2)

### 1.6 Module GNSS

Cette section présente les différents modes de fonctionnement du module GNSS ainsi que la stratégie retenue pour en réduire la consommation énergétique. En effet, ce sous-système figure parmi les plus énergivores de l’architecture et nécessite donc une attention particulière. Le choix de l’antenne est également déterminant, les signaux GNSS reçus étant de très faible puissance et particulièrement sensibles aux perturbations.

### 1.6.1 Types de démarrage

Les récepteurs GNSS distinguent trois modes de démarrage selon les informations disponibles à la mise sous tension :

- Cold start : le récepteur ne dispose d’aucune information préalable (heure, dernière position, et éphémérides³
). Il doit alors rechercher les satellites visibles, synchroniser leurs signaux et télécharger les données nécessaires au calcul de position. Cette procédure conduit à un TTFF⁴
typiquement de l’ordre de 30 secondes et à une sensibilité réduite du récepteur (-148dBm).
- Warm start : le récepteur conserve une estimation de l’heure, de la dernière position connue ainsi que des informations globales sur la constellation. Les éphémérides précédemment mémorisées étant généralement plus valides après quelques heures, elles doivent être téléchargées à nouveau. Le TTFF est alors réduit à quelques secondes et le récepteur dispose d’une bien meilleure sensibilité (-165dBm).
- Hot start : le récepteur dispose encore de données de navigation récentes et valides, notamment des éphémérides. Le redémarrage est quasi immédiat et ne nécessite pas de téléchargement complémentaire. Pour le module MAX-M10M, le TTFF typique est de l’ordre de 1 seconde avec une sensibilité de -165dBm.

Les informations utilisées pour accélérer le redémarrage sont conservées dans la Battery-Backed RAM (BBR) du module. En cas de perte d’alimentation de cette mémoire, ces données sont effacées et le module redémarre en cold start.

### 1.6.2 Gestion de l’alimentation du module GNSS

Les signaux GNSS étant fortement atténués par l’eau de mer dès quelques centimètres de profondeur, aucune réception exploitable n’est possible durant l’immersion. Afin de limiter la consommation pendant cette phase, le module est placé en mode deep sleep via le Software Standby Mode. Dans ce mode, l’alimentation interne est désactivée et le module suspend toute acquisition satellite.
Il est par contre impératif de maintenir l’alimentation du module GNSS (pin V _IO) qui permet de conserver la mémoire BBR et l’horloge temp réel (RTC). Le GPS évitera ainsi un cold start au redémarrage ce qui permet un TTFF beaucoup plus rapide, un consommation réduite et également une sensibilité du récepteur bien meilleure (gain de 20dBm environ).

En pratique, le module reste en Software Standby Mode durant l’immersion avec V _IO maintenue en permanence ce qui représente une consommation d’environ 45µA. Cette architecture permet un redémarrage en warm start à chaque remontée en surface.

### 1.6.3 Antenne du GNSS

L’antenne constitue un paramètre critique du récepteur GNSS : même le meilleur récepteur ne peut compenser les pertes engendrées par une antenne de mauvaise qualité ou une conception RF défaillante du PCB. Au-delà du choix et de la conception de l’antenne, son positionnement ainsi que l’environnement dans lequel elle opère peuvent impacter significativement ses performances.
Ainsi, pour garantir des performances optimales, le choix de l’antenne doit être guidé par les critères suivants :

3Données orbitales précises transmises par les satellites et décrivant leur trajectoire instantanée.
4Time To First Fix, temps nécessaire après la mise sous tension pour obtenir une position et une heure valides à partir d’au moins quatre satellites.

1. Faible directivité : l’antenne doit présenter un diagramme de rayonnement suffisamment large afin de capter le plus grand nombre possible de satellites.
2. Gain orienté vers le ciel : Le gain de l’antenne doit être concentré vers la demi-sphère supérieure afin d’améliorer la sensibilité du récepteur.
3. Visibilité ciel dégagée : L’antenne doit être positionnée de manière à disposer d’une vue dégagée vers le ciel, à l’écart de tout élément susceptible de perturber le champ électromagnétique, tel que des pièces métalliques ou des structures conductrices.
4. Adaptation d’impédance : l’impédance entre l’antenne, la ligne de transmission et l’entrée RF du récepteur GNSS doit être correctement adaptée (généralement à 50Ω) afin de minimiser les réflexions et maximiser le transfert de puissance.

Dans une optique de réduction de la consommation énergétique, le choix s’est porté sur une antenne patch passive. Ce choix se justifie principalement par l’absence de consommation propre à l’antenne, contrairement aux antennes actives qui intègrent un Low Noise Amplifier (LNA), dont la consommation se situe typiquement entre 3 et 20mA. Ce dernier permet néanmoins d’obtenir un gain plus élevé pour des dimensions plus compactes.
L’antenne patch passive, dépourvue d’amplification intégrée, impose en revanche une conception RF plus rigoureuse, notamment en raison d’une sensibilité accrue aux désadaptations d’impédance. Par ailleurs, ce type d’antenne nécessite un plan de masse de dimensions suffisantes afin d’assurer un gain satisfaisant ainsi qu’une directivité orientée vers le ciel. Plus ce plan de masse est réduit, plus les performances de l’antenne (gain, efficacité, rayonnement) se dégradent.


Figure 3: Image de l’antenne patch chosie pour le récepteur GNSS

### 1.6.4 Performances de l’antenne GNSS choisie

Une antenne patch de chez Quectel a été retenue en raison de son large plan de masse (40 mm x 40 mm) (cf. fig. 3). Celui-ci permet d’améliorer les performances de l’antenne patch en favorisant une directivité principalement orientée vers le ciel et en augmentant son gain (gain maximale de 0.58dBi), comme illustré aux figures 4 et 5.
L’antenne patch étant destinée à être montée à plat, orientée vers le ciel, tout rayonnement non dirigé dans cette direction constitue une perte d’énergie. C’est précisément pour cette raison que cette antenne se révèle particulièrement adaptée à l’application visée. Elle satisfait aux exigences GNSS en offrant un bon compromis entre gain et couverture angulaire.

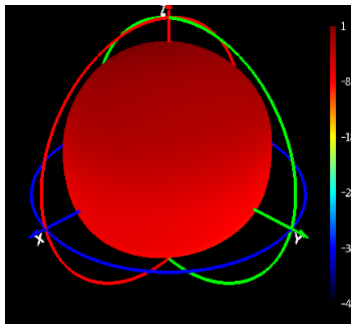
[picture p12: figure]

Figure 4: Diagramme de rayonnement de l’antenne à la fréquence de 1575MHz (free space)


Figure 5: Directivité de l’antenne à Phi=0 degré et à une fréquence de 1575MHz (free space)

La caractérisation complète d’une antenne ne saurait se limiter à l’analyse du diagramme de rayonnement et de la directivité ; l’adaptation d’impédance constitue également un paramètre fondamental. Ce dernier permet d’évaluer la proportion du signal réellement transmise au module GNSS. Il se mesure à l’aide d’un Vector Network Analyzer (VNA).


Figure 6: Paramètre S11 de l’antenne | Figure 7: Smith Cart de l’antenne

D’après la figure 6, le paramètre S11 à 1.575GHz vaut -15.09dB, ce qui permet de déterminer le coefficient de réflexion Γ :

S11 = 10log(Γ) = −15.09dB ⇔ Γ = Pref lechie

Ptransmise

= 0.03 | (3)

Ce résultat indique que 97% de la puissance incidente est transmise au récepteur GNSS, ce qui témoigne d’une excellente adaptation d’impédance.
L’impédance d’entrée de l’antenne peut alors être calculée à partir de Γ (équation 3) :

Zant = Z0

1 + Γ
1 − Γ
= 53.09Ω | (4)

Cette valeur est proche de l’objectif nominal de 50 Ω. Ce résultat est également visible sur la carte de Smith : le marqueur 3, correspondant à la fréquence GNSS étudiée, est situé à proximité du centre de la carte, zone caractéristique d’une adaptation optimale (absence de réflexion).
Enfin, la figure 6 permet également d’estimer la bande passante de l’antenne, définie conventionnellement par le critère S11 < −10 dB. À l’aide des marqueurs 1 et 4, la bande passante obtenue est d’environ 10.25 MHz.

### 1.7 Conception du PCB

La conception du PCB a constitué une étape critique du projet. Une attention particulière a donc été portée au dimensionnement de l’alimentation, à la dissipation thermique et au routage de la piste RF du module GNSS.

### 1.7.1 Dimensionnement de l’alimentation

L’alimentation du PCB a été conçue pour supporter les pics de courants des modules de communication satellite et GNSS pouvant atteindre plusieurs centaines de milliampères sur de courtes durées. Si elle est mal dimensionné elle pourrait ne pas fournir ces appels de courants ou alors provoquer des chutes de tension susceptibles d’entrainer des dysfonctionnements.
Le choix des régulateurs, le routage des pistes d’alimentation ainsi que le découplage a été réalisé de manière à garantir une alimentation stable.

Table 4: Pics de courants des modules satellite et GNSS

Module | Peak current
Satellite GNSS | 400mA 100mA

Le régulateur MCP1726 a ainsi été sélectionné pour sa capacité à fournir jusqu’à 1A, garantissant ainsi une marge suffisante face aux pics de courant estimés à 500mA. Il convient également de vérifier que le package retenu permet de dissiper correctement la chaleur générée, sans dépasser la température de jonction maximale admissible de 125°C (valeur tirée de la datasheet).

La puissance dissipée en interne par le LDO est donnée par :

PLDO = (VIN(max) − VOUT ) × IOUT(max) = (4.2V − 3.3V ) × 500mA = 0.45W | (5)

La température de jonction TJ est calculée selon la formule issue de la datasheet :

TJ = TA(max) + PLDO × RθJA | (6)

où RθJA est la résistance thermique junction-to-ambiant, exprimée en ◦C/W, et TA(max) = 70◦C, la température ambiante maximale supposée.

Deux packages sont disponibles pour le MCP1726 : le SOIC et le DFN. Seule ce dernier, qui dispose d’une résistance thermique bien inférieure (car il dispose d’un pad thermique) permet de respecter un température de jonction inférieur au 125◦C spécifié.

Selon l’équation 6, la température de jonction atteint avec un boitier DFN de résistance thermique RθJA = 64◦C/W se calcul ainsi :

TJ = TJRISE + TA(max) = 0.45W × 64◦C/W + 70◦C = 98.8

◦C | (7)

Ainsi le package DFN est retenu, car il est le seul à garantir une température de jonction inférieure à 125◦C

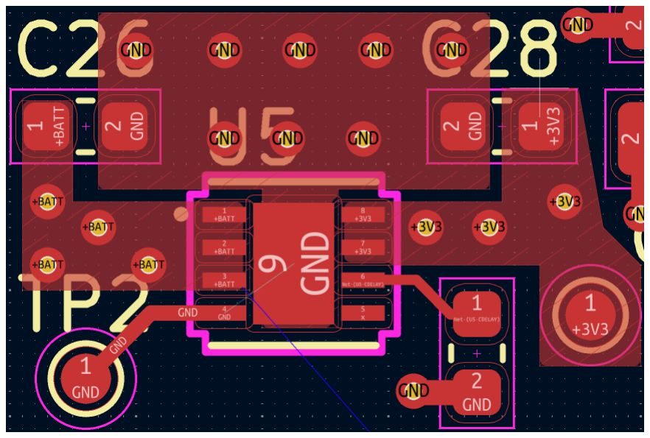
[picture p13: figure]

Figure 8: Layout du régulateur LDO de sorte à assurer une bonne dissipation thermique

### 1.7.2 Layout du module GNSS

Le signal reçu par le module GNSS est extrêmement faible, de l’ordre de 160dBm. La conception du layout RF constitue donc un point critique du PCB : toute perte ou perturbation sur la ligne RF peut dégrader significativement la sensibilité du récepteur et allonger le temps d’acquisition du signal.
Une attention particulière a été portée au routage de la liaison entre l’antenne et l’entrée RF du module. Cette ligne a été conçue comme une ligne à impédance contrôlée de 50Ω en utilisant une topologie Coplanar Waveguide with Ground (CPWG), afin d’assurer un transfert de puissance optimal et de minimiser les réflexions.


Figure 9: Layout du module GNSS

### 1.7.3 Points de tests

Enfin, plusieurs points de test ont été intégrés sur le PCB afin de faciliter l’accès aux principales alimentations, interfaces de communication et signaux critiques, simplifiant les mesures à l’oscilloscope ainsi que les phases de diagnostic.

## 2 Annexes

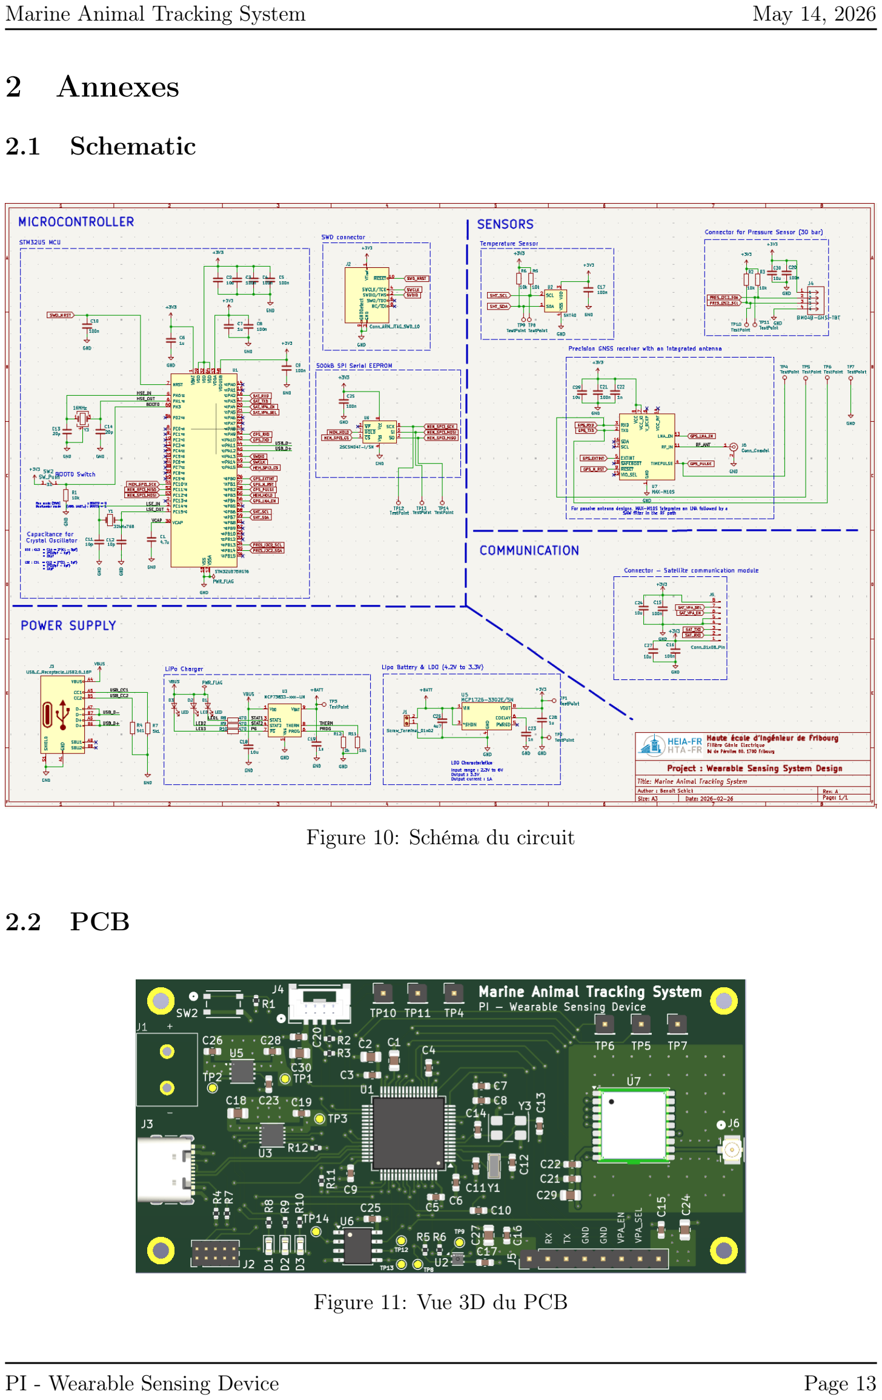
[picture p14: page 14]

### 2.1 Schematic

Figure 10: Schéma du circuit

### 2.2 PCB

Figure 11: Vue 3D du PCB

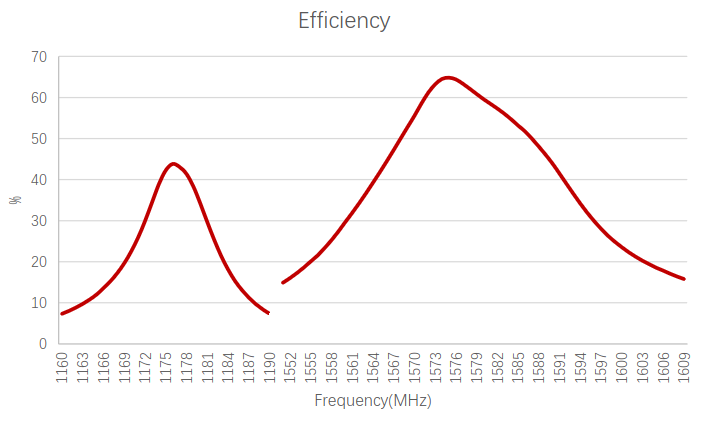
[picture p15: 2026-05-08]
report/pictures/antenne_nul/eff_avecplan.png

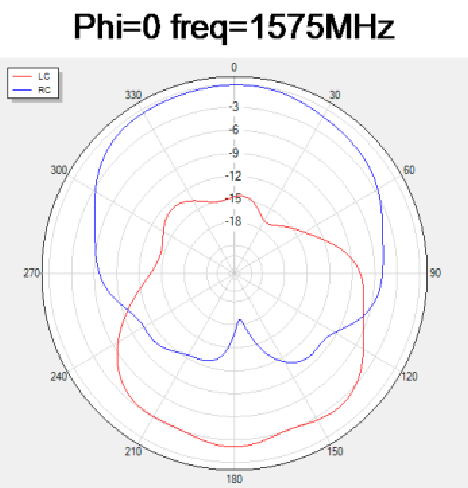
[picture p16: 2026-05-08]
report/pictures/antenne_nul/dir_avecplan.png

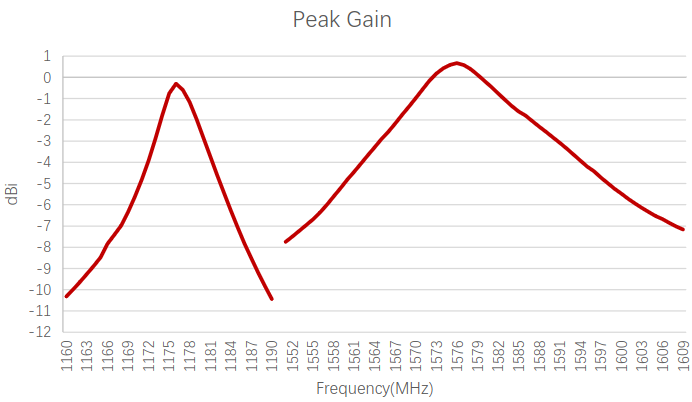
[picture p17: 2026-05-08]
report/pictures/antenne_nul/gain_avecplan.png

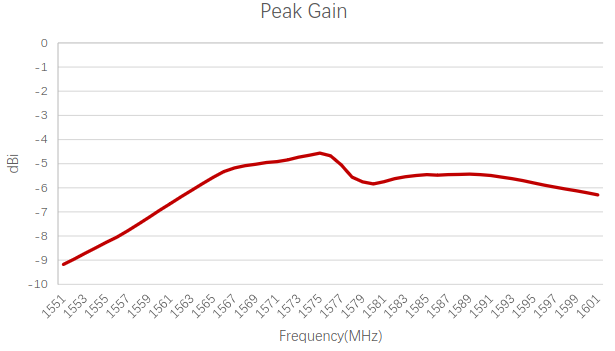
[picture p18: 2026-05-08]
report/pictures/antenne_nul/gain_sansplan.png

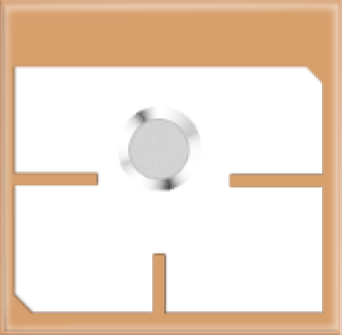
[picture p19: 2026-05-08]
report/pictures/antenne_nul/ant_sansplan.png

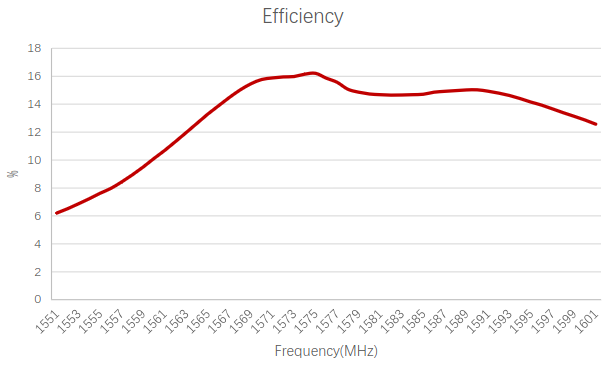
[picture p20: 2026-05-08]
report/pictures/antenne_nul/eff_sansplan.png

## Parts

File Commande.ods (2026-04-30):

Name | Qte | Manufacturer | Description | Delivery time (days) | Price (component) | Price (delivery) | Price ($) | URL
Pressure sensors | 1 | BlueRobotics |  | ? | 90 | 32 | 0 | https://bluerobotics.com/store/sensors-cameras/sensors/bar-depth-pressure-sensor/
Lipo Battery 1S | 1 | LiPoly Batteries | 3.7 V Lipo Battery 10000mAh | 7 | 17.44 | 6.45 | 23.89 | https://www.amazon.fr/Uxney-Batterie-lithium-polym%C3%A8re-lithium-ion-connecteur/dp/B0CSS4FFHC?__mk_fr_FR=%C3%85M%C3%85%C5%BD%C3%95%C3%91
Antenna | 1 | Sparkfun | ARGOS Omnidirectional Antenna - 401MHz | ? | 29.9 | 27.76 | 57.66 | https://www.sparkfun.com/argos-omnidirectional-antenna-401mhz.html
YFGA225E3BM | 1 | Quectel | EMBEDDED ANTENNA | 2 | 9.9 | 20 | 29.9 | https://www.digikey.ch/en/products/detail/quectel/YFGA225E3BM/26239589
Arribada SMD Wing | 1 | Arribada | Satellite communication module | ? | 84.99 | 18 | 102.99 | https://arribada.org/product/arribada-smd-wing/
PCB Manufacture + Assembly | 1 |  |  | 30-35 | 94 |  | 94
Boitier |  |  |  |  |  |  | 192
 |  |  |  | Total |  |  | 500.44
 |  |  |  |  |  |  | 500.44
 |  |  |  |  |  |  | 308.44

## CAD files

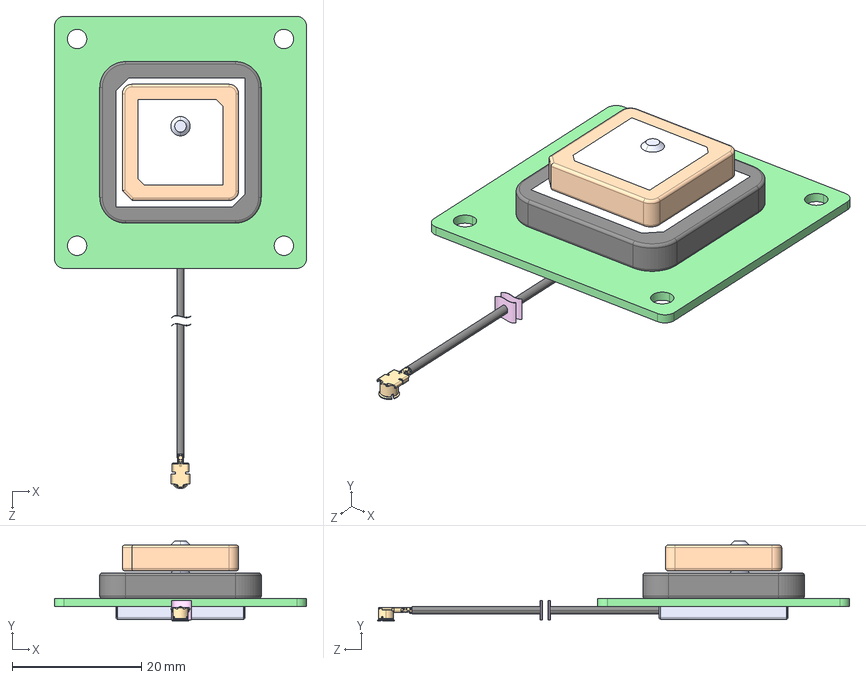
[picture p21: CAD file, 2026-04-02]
Step_file/YFGA225E3BM.STEP
39.0 x 12.3 x 73.1 mm
YFGA225E3BM_YFGA225E3BM
MHF 1 (2.1mm)
RF1.13 Cable^YFGA225E3BM ass_RF1.13 Cable
YFGA225E3BM-custom_YFGA225E3BM

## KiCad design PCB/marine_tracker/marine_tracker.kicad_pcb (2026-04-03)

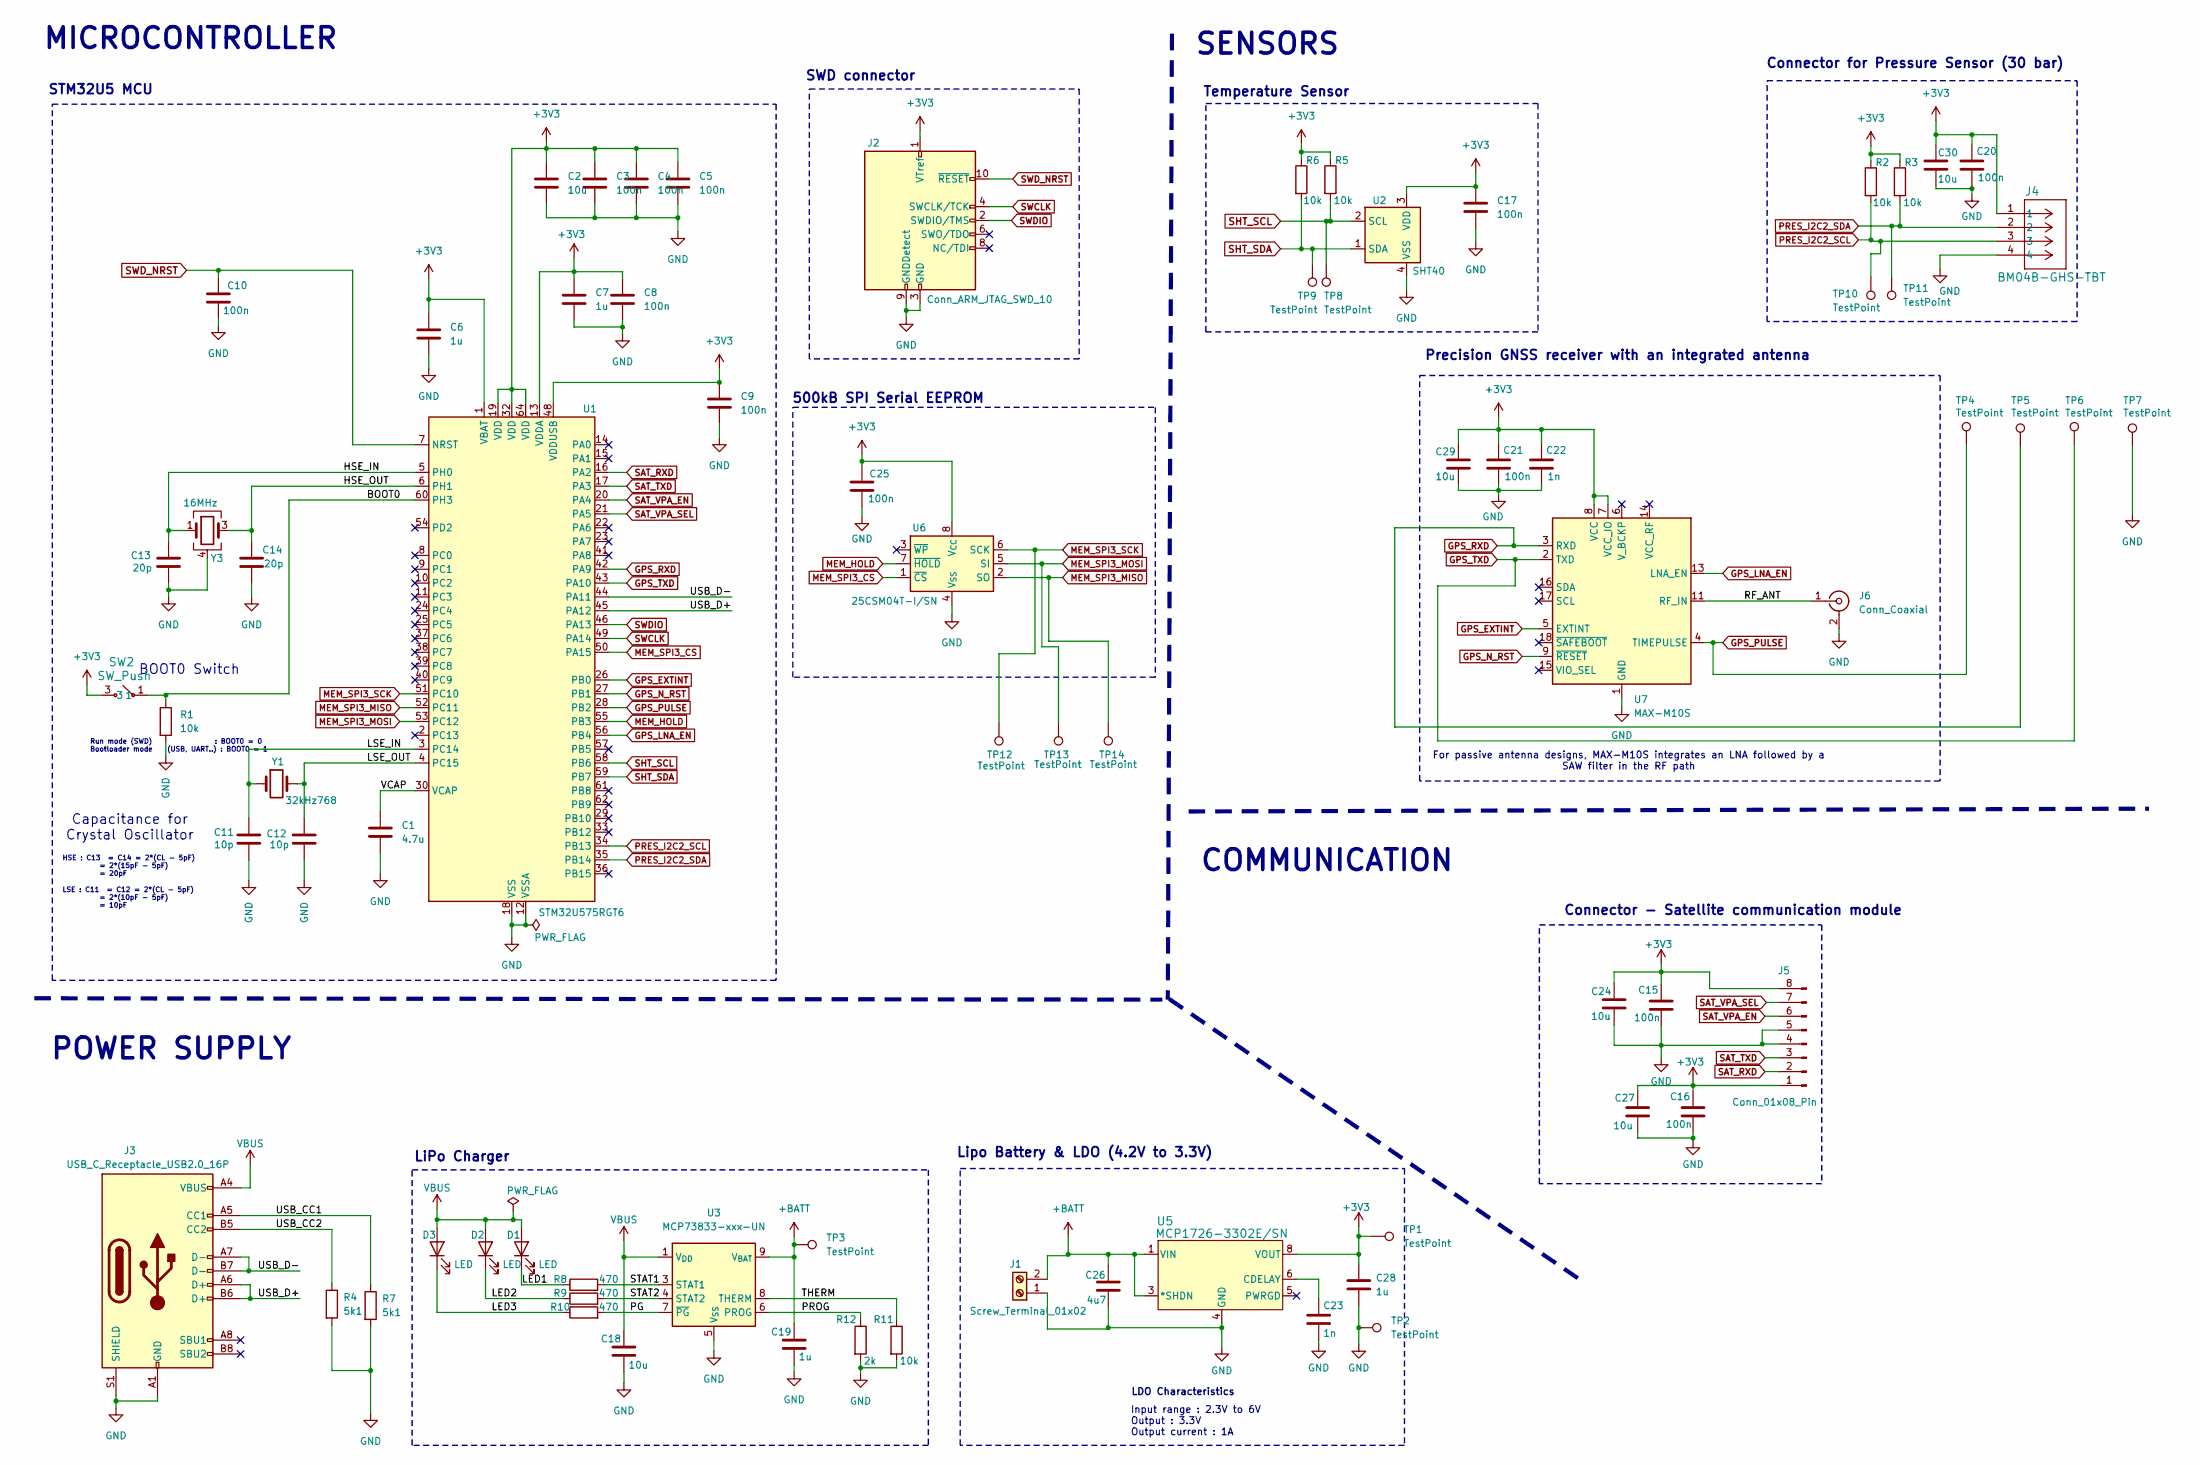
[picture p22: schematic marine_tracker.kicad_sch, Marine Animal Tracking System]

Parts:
C1: 4.7u; C_0805_2012Metric; Manufacturer Part Number CC0805ZKY5V7BB475; Digikey Part Number 311-1907-2-ND
C2, C18, C24, C27, C29, C30: 10u; C_0805_2012Metric; Manufacturer Part Number CC0805KRX5R7BB106; Digikey Part Number 311-3502-2-ND
C3, C4, C5, C8, C9, C10, C15, C16, C17, C20, C21, C25: 100n; C_0603_1608Metric; Manufacturer Part Number CC0603KRX7R7BB104; Digikey Part Number 311-1088-2-ND
C6, C7, C19, C28: 1u; C_0603_1608Metric; Manufacturer Part Number CC0603KRX7R7BB105; Digikey Part Number 311-1446-2-ND
C11, C12: 10p; C_0603_1608Metric; Manufacturer Part Number CC0603JRNPO9BN100; Digikey Part Number 311-1058-2-ND
C13, C14: 20p; C_0603_1608Metric; Manufacturer Part Number CC0603JRNPO0BN200; Digikey Part Number 311-1754-2-ND
C22, C23: 1n; C_0603_1608Metric; Manufacturer Part Number CC0603JPNPO9BN102; Digikey Part Number 13-CC0603JPNPO9BN102TR-ND
C26: 4u7; C_0603_1608Metric; Manufacturer Part Number CC0603KRX5R7BB475; Digikey Part Number 311-1785-2-ND
D1, D2, D3: LED; LED_0603_1608Metric; Manufacturer Part Number SML-D12U1WT86; Digikey Part Number SML-D12U1WT86TR-ND
J1: Screw_Terminal_01x02; Screw_terminal_1x2; Manufacturer Part Number 691137710002; Digikey Part Number 732-10955-ND
J2: Conn_ARM_JTAG_SWD_10; PinHeader_2x05_P1.27mm_Vertical; Manufacturer Part Number 20021111-00010T4LF; Digikey Part Number 609-3712-ND
J3: USB_C_Receptacle_USB2.0_16P; USB_C_Receptacle_GCT_USB4105-xx-A_16P_TopMnt_Horizontal; Manufacturer Part Number USB4215-03-A; Digikey Part Number 2073-USB4215-03-ATR-ND
J4: BM04B-GHS-TBT; CONN_BM04B-GHS-TBT_JST; Manufacturer Part Number BM04B-GHS-TBT; Digikey Part Number 455-BM04B-GHS-TBTTR-ND
J5: Conn_01x08_Pin; PinHeader_1x08_P2.54mm_Vertical; Manufacturer Part Number 61300811121; Digikey Part Number 732-5321-ND
J6: Conn_Coaxial; CONN_UFL_RSP-122811-01_SAI; Manufacturer Part Number RSP-122811-01; Digikey Part Number 612-RSP-122811-01TR-ND
R1, R2, R3, R5, R6, R11: 10k; R_0402_1005Metric; Manufacturer Part Number RC0402FR-0710KL; Digikey Part Number 311-10.0KLRTR-ND
R4, R7: 5k1; R_0402_1005Metric; Manufacturer Part Number RC0402FR-075K1L; Digikey Part Number 311-5.10KLRTR-ND
R8, R9, R10: 470; R_0402_1005Metric; Manufacturer Part Number RC0402FR-07470RL; Digikey Part Number 311-470LRTR-ND
R12: 2k; R_0402_1005Metric; Manufacturer Part Number RC0402FR-072KL; Digikey Part Number 311-2KLRTR-ND
SW2: SW_Push; SW4_PTS815 SJM 250 SMTR LFS_CNK_btnPoussoir; Manufacturer Part Number PTS815SJM250SMTRLFS; Digikey Part Number CKN12215-2-ND
TP1, TP2, TP3, TP8, TP9, TP12, TP13, TP14: TestPoint; TestPoint_Pad_D1.0mm
TP4, TP5, TP6, TP7, TP10, TP11: TestPoint; PinHeader_1x01_P2.54mm_Vertical
U1: STM32U575RGT6; LQFP-64_10x10mm_P0.5mm; Manufacturer Part Number STM32U575RGT6; Digikey Part Number 497-STM32U575RGT6-ND
U2: SHT40; Sensirion_DFN-4_1.5x1.5mm_P0.8mm_SHT4x_NoCentralPad; Manufacturer Part Number SHT40-AD1B-R3; Digikey Part Number 1649-SHT40-AD1B-R3TR-ND
U3: MCP73833-xxx-UN; lipo_charger; Manufacturer Part Number MCP73833T-FCI/MF; Digikey Part Number MCP73833T-FCI/MFTR-ND
U5: MCP1726-3302E/SN; LDO_1A; Manufacturer Part Number MCP1726-3302E/MF; Digikey Part Number MCP1726-3302E/MF-ND
U6: 25CSM04T-I/SN; JEITA_SOIC-8_3.9x4.9mm_P1.27mm; Manufacturer Part Number 25CSM04T-I/SN; Digikey Part Number 150-25CSM04T-I/SNTR-ND
U7: MAX-M10S; ublox_MAX; Manufacturer Part Number MAX-M10S-00B; Digikey Part Number 672-MAX-M10S-00BTR-ND
Y1: 32kHz768; Crystal_SMD_3215-2Pin_3.2x1.5mm; Manufacturer Part Number FC-135R 32.7680KA-A3; Digikey Part Number SER4071TR-ND
Y3: 16MHz; Crystal_SMD_5032-4Pin_5.0x3.2mm; Manufacturer Part Number X1G0044510002; Digikey Part Number SER4396TR-ND

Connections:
+3V3: C2.1, C3.1, C4.1, C5.1, C6.1, C7.1, C8.1, C9.1, C15.1, C16.1, C17.1, C20.1, C21.1, C22.1, C24.1, C25.1, C27.1, C28.1, C29.1, C30.1, J2.1 (VTref), J4.1, J5.1, J5.8, R2.1, R3.1, R5.1, R6.1, SW2.3, SW2.4, TP1.1, U1.1 (VBAT), U1.13 (VDDA), U1.19 (VDD), U1.32 (VDD), U1.48 (VDDUSB), U1.64 (VDD), U2.3 (VDD), U5.7 (VOUT), U5.8 (VOUT), U6.8 (V_{CC}), U7.7 (VCC_IO), U7.8 (VCC)
+BATT: C19.1, C26.1, J1.2, TP3.1, U3.9 (V_{BAT}), U3.10 (V_{BAT}), U5.1 (VIN), U5.2 (VIN), U5.3 (*SHDN)
/BOOT0: R1.1, SW2.1, SW2.2, U1.60 (PH3)
/HSE_IN: C13.2, U1.5 (PH0), Y3.1
/HSE_OUT: C14.2, U1.6 (PH1), Y3.3
/LED1: D1.1 (K), R8.1
/LED2: D2.1 (K), R9.1
/LED3: D3.1 (K), R10.1
/LSE_IN: C11.2, U1.3 (PC14), Y1.1
/LSE_OUT: C12.2, U1.4 (PC15), Y1.2
/PG: R10.2, U3.7 (~PG)
/PROG: R12.1, U3.6 (PROG)
/RF_ANT: J6.1 (In), U7.11 (RF_IN)
/STAT1: R8.2, U3.3 (STAT1)
/STAT2: R9.2, U3.4 (STAT2)
/THERM: R11.1, U3.8 (THERM)
/USB_CC1: J3.A5 (CC1), R7.1
/USB_CC2: J3.B5 (CC2), R4.1
/USB_D+: J3.A6 (D+), J3.B6 (D+), U1.45 (PA12)
/USB_D-: J3.A7 (D-), J3.B7 (D-), U1.44 (PA11)
/VCAP: C1.1, U1.30 (VCAP)
GND: C1.2, C2.2, C3.2, C4.2, C5.2, C6.2, C7.2, C8.2, C9.2, C10.2, C11.1, C12.1, C13.1, C14.1, C15.2, C16.2, C17.2, C18.2, C19.2, C20.2, C21.2, C22.2, C23.2, C24.2, C25.2, C26.2, C27.2, C28.2, C29.2, C30.2, J1.1, J2.3 (GND), J2.5 (GND), J2.9 (GNDDetect), J3.A1 (GND), J3.A12 (GND), J3.B1 (GND), J3.B12 (GND), J3.S1 (SHIELD), J4.4, J5.4, J5.5, J6.2 (Ext), J6.3 (Ext2), R1.2, R4.2, R7.2, R11.2, R12.2, TP2.1, TP7.1, U1.12 (VSSA), U1.18 (VSS), U1.31 (VSS), U1.47 (VSS), U1.63 (VSS), U2.4 (VSS), U3.5 (V_{SS}), U3.11 (EP), U5.4 (GND), U5.9 (EP), U6.4 (V_{SS}), U7.1 (GND), U7.10 (GND), U7.12 (GND), Y3.2, Y3.4 (G)
GPS_EXTINT: U1.26 (PB0), U7.5 (EXTINT)
GPS_LNA_EN: U1.56 (PB4), U7.13 (LNA_EN)
GPS_N_RST: U1.27 (PB1), U7.9 (~RESET)
GPS_PULSE: TP4.1, U1.28 (PB2), U7.4 (TIMEPULSE)
GPS_RXD: TP5.1, U1.42 (PA9), U7.3 (RXD)
GPS_TXD: TP6.1, U1.43 (PA10), U7.2 (TXD)
MEM_HOLD: U1.55 (PB3), U6.7 (~HOLD)
MEM_SPI3_CS: U1.50 (PA15), U6.1 (~CS)
MEM_SPI3_MISO: TP14.1, U1.52 (PC11), U6.2 (SO)
MEM_SPI3_MOSI: TP13.1, U1.53 (PC12), U6.5 (SI)
MEM_SPI3_SCK: TP12.1, U1.51 (PC10), U6.6 (SCK)
unnamed: C23.1, U5.6 (CDELAY)
PRES_I2C2_SCL: J4.3, R2.2, TP10.1, U1.34 (PB13)
PRES_I2C2_SDA: J4.2, R3.2, TP11.1, U1.35 (PB14)
SAT_RXD: J5.2, U1.16 (PA2)
SAT_TXD: J5.3, U1.17 (PA3)
SAT_VPA_EN: J5.6, U1.20 (PA4)
SAT_VPA_SEL: J5.7, U1.21 (PA5)
SHT_SCL: R5.2, TP8.1, U1.58 (PB6), U2.2 (SCL)
SHT_SDA: R6.2, TP9.1, U1.59 (PB7), U2.1 (SDA)
SWCLK: J2.4 (SWCLK/TCK), U1.49 (PA14)
SWDIO: J2.2 (SWDIO/TMS), U1.46 (PA13)
SWD_NRST: C10.1, J2.10 (~RESET), U1.7 (NRST)
VBUS: C18.1, D1.2 (A), D2.2 (A), D3.2 (A), J3.A4 (VBUS), J3.A9 (VBUS), J3.B4 (VBUS), J3.B9 (VBUS), U3.1 (V_{DD}), U3.2 (V_{DD})

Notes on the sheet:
SWD connector
Lipo Battery & LDO (4.2V to 3.3V)
HSE : C13 = C14 = 2*(CL - 5pF) = 2*(15pF - 5pF) = 20pF
LSE : C11 = C12 = 2*(CL - 5pF) = 2*(10pF - 5pF) = 10pF
Precision GNSS receiver with an integrated antenna
POWER SUPPLY
STM32U5 MCU
Capacitance for Crystal Oscillator
SENSORS
LDO Characteristics
LiPo Charger
COMMUNICATION
For passive antenna designs, MAX-M10S integrates an LNA followed by a SAW filter in the RF path
MICROCONTROLLER
BOOT0 Switch
Connector - Satellite communication module
Run mode (SWD) : BOOT0 = 0 Bootloader mode (USB, UART..) : BOOT0 = 1
Input range : 2.3V to 6V Output : 3.3V Output current : 1A
500kB SPI Serial EEPROM
Connector for Pressure Sensor (30 bar)
Temperature Sensor

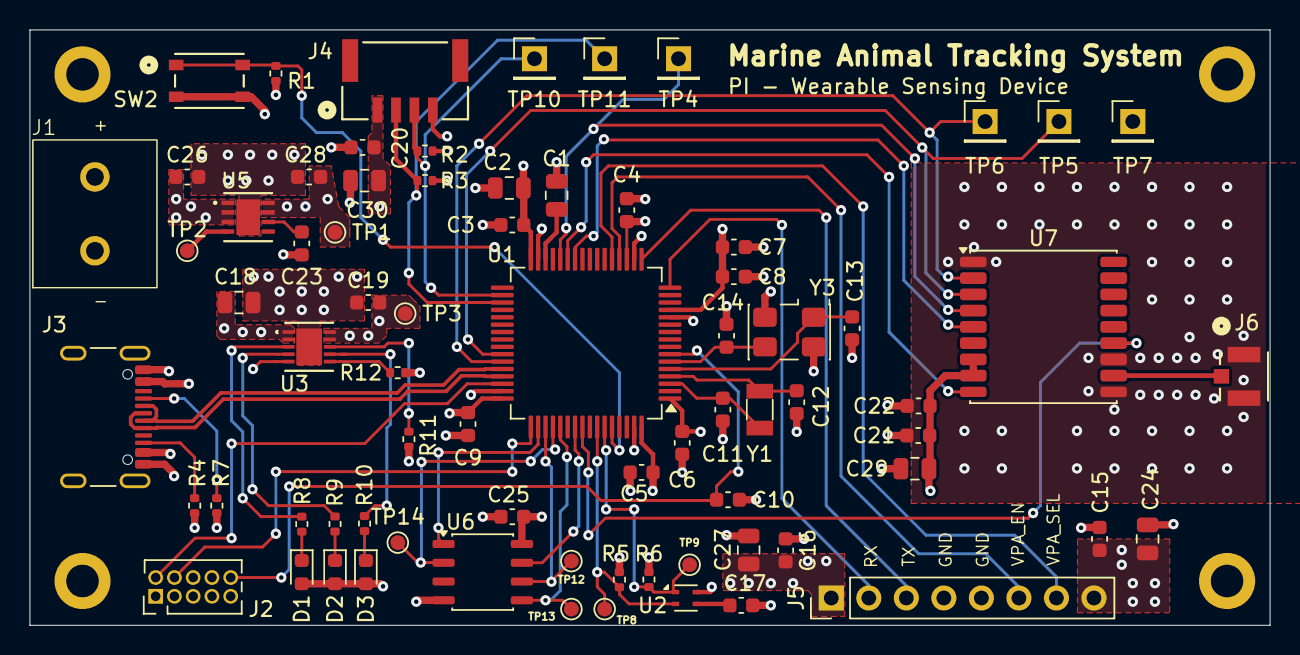
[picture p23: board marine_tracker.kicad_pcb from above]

Board: 4 copper layers, 83.9 x 40.3 mm, 74 parts (0 on the bottom side), 46 nets.

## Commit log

2026-02-27 STM32 Schematic finished
    [marine_tracker.kicad_sch]
2026-03-01 update schematics
    [AST50127-00.stp, marine_tracker.kicad_sch]
2026-03-01 schematics update
    [marine_tracker.kicad_sch]
2026-03-05 add screw terminal for battery
    [marine_tracker.kicad_sch]
2026-03-05 add new connector for pressure sensor
    [marine_tracker.kicad_pcb, marine_tracker.kicad_sch]
2026-03-05 add connector for satellite communication module
    [marine_tracker.kicad_pcb, marine_tracker.kicad_sch]
2026-03-05 add 3D models
    [RockBLOCK_V_3B.STEP, marine_tracker.kicad_pcb, marine_tracker.kicad_sch]
2026-03-06 Component Placement + export Step file PCB
    [RockBLOCK_V_3B.STEP, marine_tracker.kicad_pcb, marine_tracker.kicad_sch]
2026-03-19 routage + change GNSS module + add decoupling capacitor + change 0200/0400 package to 0600 package
    [AST50127-00.stp, marine_tracker.kicad_pcb, marine_tracker.kicad_sch]
2026-03-19 PCB routage WIP
    [marine_tracker.kicad_pcb, marine_tracker.kicad_sch]
2026-03-23 add new connector for Satellite module + new LDO regulator with an maximum current higher
    [marine_tracker.kicad_pcb, marine_tracker.kicad_sch]
2026-03-26 change to UFL connector + add stiching via
    [marine_tracker.kicad_pcb, marine_tracker.kicad_sch]
2026-03-26 drc violation PCB corrected
    [YFGA025E3DM.STEP, marine_tracker.kicad_pcb]
2026-03-29 add reference to symbols
    [marine_tracker.kicad_pcb, marine_tracker.kicad_sch]
2026-03-31 correction PCB
    [marine_tracker.kicad_pcb, marine_tracker.kicad_sch]
2026-03-31 PCB finish
    [marine_tracker.kicad_pcb]
2026-03-31 adapt silkscreen
    [marine_tracker.kicad_pcb]
2026-04-02 final review + add part number
    [marine_tracker.kicad_pcb, marine_tracker.kicad_sch]
2026-04-02 resolve DRC violation
    [RockBLOCK_V_3B.STEP, YFGA025E3DM.STEP, YFGA225E3BM.STEP, external_BOM.ods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]
2026-04-03 adding testpoint
    [external_BOM.ods, marine_tracker-B_Cu.gbr, marine_tracker-B_Mask.gbr, marine_tracker-B_Paste.gbr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]
2026-04-30 writting report
    [marine_tracker-B_Cu.gbr, marine_tracker-B_Mask.gbr, marine_tracker-B_Paste.gbr, marine_tracker-B_SilkS.gbr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]
